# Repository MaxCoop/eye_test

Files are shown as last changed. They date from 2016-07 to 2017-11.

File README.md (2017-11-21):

# Pupil measurement device 
## System overview 
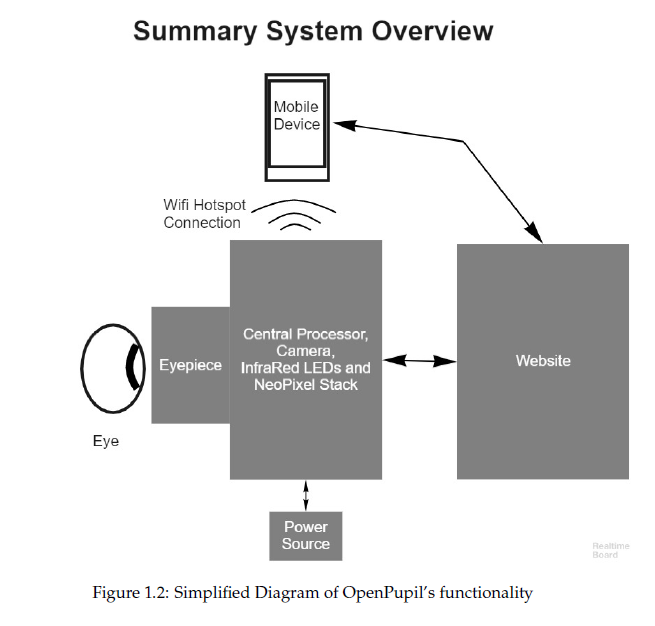
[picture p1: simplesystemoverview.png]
System

Format: 

# System description

Our system uses a RPi 2 B+ as a base along with a NoIR camera to recieve images of the pupil illuminated under IR light. RPi setup instuctions [here](https://github.com/kaiwhata/eye_test/blob/master/RPi_setup.md). Our continous integration and testing pipline is detailed [here](https://github.com/kaiwhata/eye_test/blob/master/testing.md). We use neopixel rings to illuminate the eye with visible light and them image process the camera frame stream to measure the pupil size based of several different algorithms (listed below). The Rpi acts as its own wifi hotspot for the 'Openpupil' network. Once connected to the network, the device is controlled by a python flask webapp acessible through a browser at the ip address `192.168.42.1:5000/`. The flask webapp code is contained within the `app.py` file, whereas site dynamics are controlled via javascript in the `index.html` and calls some additional javascript functions from the `extra.js` file. The webapp can be launched by running the command `sudo python app.py` from inside the webapp directory. We also use `supervisor-ctl` to run this app at boot by default.  

# Software process

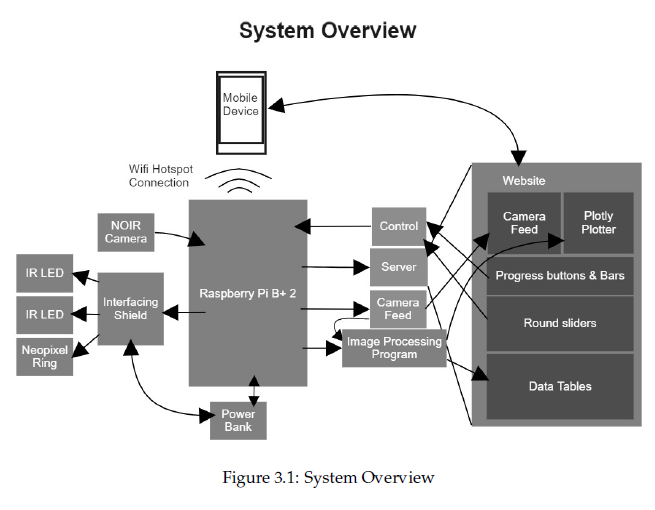
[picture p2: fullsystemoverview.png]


```
.
+-- _Webapp
|   +-- RunMe.sh
|   +-- App.py
|   +-- camera.py
|   +-- camera_pi.py
|   +-- _python
|   |   +-- NeopixelColorControl.py
|   |   +-- data_plotting.py
|   +-- _templates
|   |   +-- index.html
|   +-- _Data
|   |   +-- <date_named_data_folders>
|   +-- _static
|   |   +-- _js
|   |   |   +-- extra.js
|   |   |   +-- script.js
|   |   +-- _css
|   |   +-- _dist
|   |   +-- _images
|   |   +-- _scripts
|   |   +-- _src
+-- _Snapshot
```

## Supervisor
We use supervisor-ctl to launch the flask webserverapp at boot.
Scripts are called automatically from the `supervisord.conf` file and running the `supervisorctl status all` command will show what scripts/p[rograms are currently known by and teh status of them under supervior.

## Scripts
Main script is `RunMe.sh` which currently uses the `/CCodeVid5` command for ?? fps image capture and generates datafiles in teh data directory based on time and date. Illumintation is controlled by and calling the script `neopixel_elf.py` from the neopixel driver directory to perform the specific light sequences. 

## Video frame processing
Currently frames are parsed directly from the rpi camers by the CCodeVid5.cpp method  
The process sequence is performed using OpenCV methods:
  - extract red channel
  - binary thresholding - `threshold(50)` but dynamically calculated from the darkest 6000 pixels
  - count number of black pixels after thresholding (analog of pupil area)
  - estimate centre location of pupil and pupil width and height each frame based of x and y intensity histograms
  - in the past we have also attempted canny edge detction followed by hough circle fitting
  - ultimately we will also implements Kaps' spiral edge following code for higher resolution and faster measurement 

# Hardware System description
System designs and code for a cheap pupil measurement device that is capable of fabrication and use by non-technical people.
Current system design uses a 3D printed google (the OpenSCAD files), and a 16 neopixel ring for colour specific illumination, two wide angle IR LEDs controlled using a transistor and a 15 Ohm resistor.  IR LED is driven by GPIO pin 4, Neopixels are driven from GPIO 18. The google also contains the lens from a Google cardboard and photographic negative film to block visible light to the NoIR camera used for image capture.

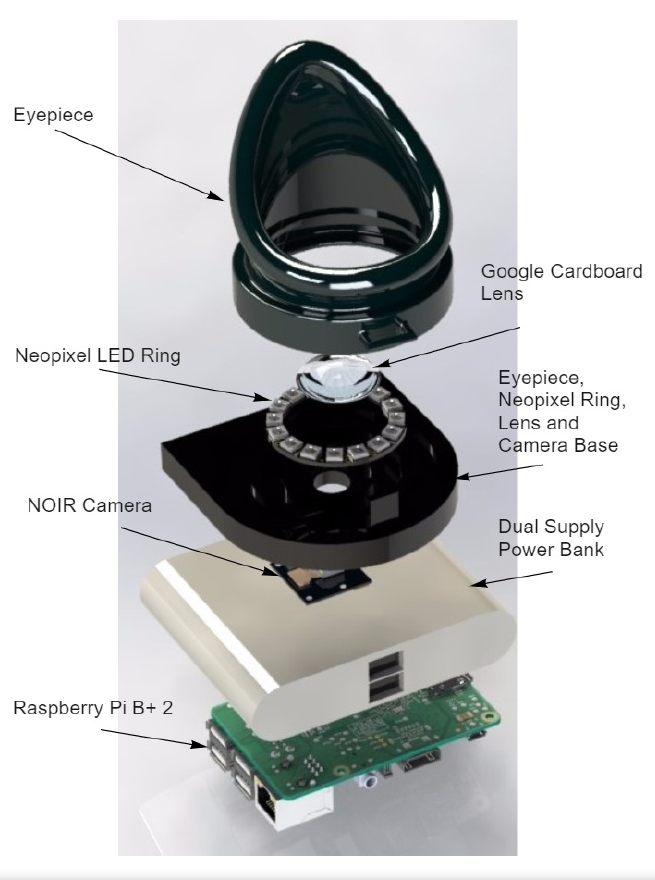
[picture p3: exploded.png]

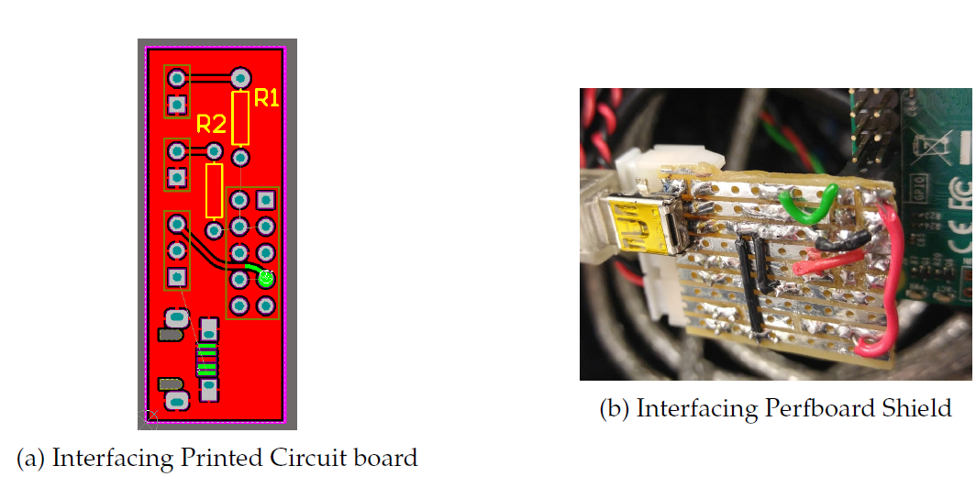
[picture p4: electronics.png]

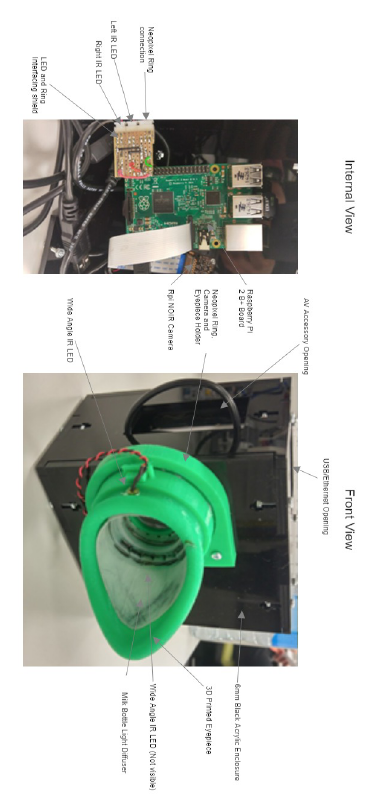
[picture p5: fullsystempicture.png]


Neopixels used in this project have the datasheet from here - https://cdn-shop.adafruit.com/datasheets/WS2812.pdf

Intensity measurement for blue light = 200-400 mCD (milliCandela) according to the Neopixel datasheet

3D Model for Neopixel used in this project can be found here: https://grabcad.com/library/neopixelring-16x-1/details?folder_id=1182174

3D Model for Eyepiece used in this project can be found here: https://grabcad.com/library/eyecup

3D Model for Raspberry Pi used in Assembly can be found here: https://grabcad.com/library/raspberry-pi-model-b-2

System uses Raspberry PI 2 B. Pinout used here -> http://pi4j.com/images/j8header-2b-large.png

### To Do
 - fix security an permissions (sudo) issues
 - improve javascript app load time by caching
 - upgrades to binocularity via multiplexer and multiple neopixel rings
 - implement spiral edge detection alcorithing for `CCodeVid6.cpp`
 - fix bug where preview button locks camera process
 - the 'measure' button needs 'close preview' functionality added to it so that it frees the camera for CCodeVid analysis
  
Credit to Dr. Jesse Gale for original concept and implementation idea. To Kapetini Polutea for the image processing code and algorithims. To Shaetrun Pathmanathan for the electronics and hardware redesign and for the web interface and javascript.

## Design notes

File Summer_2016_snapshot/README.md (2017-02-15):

# Pupil measurement device

#Dec 2016 update

#Software process

Experimentation has shown that for low resolution videos (480p, 720p, 1080p) the number of black pixels is a slow and innacurate method of pupil mesurement. Whilst improvments to the eyepiece (specifically the addition of another IR led) has improved thresholding it appears very noisy compared to full resolution data.

Current experiments have implemented the Hough circle dection algorithm 9using canny edge detection) to detect a single circle in our original image (code in `measure_pupil_hough.py`). We expect this to be unusably slow on the Rpi.

Kaps has implemented image capture and near real-time processing on 480p video `CCodeVid2.cpp`. OUr current pupil detection algotithim has an unacceptable signal to noise ratio in these low resolution videos. 

# Image processing
Currently images are parsed by the `measure_pupil_hough.py` script [`python measure_pupil_hough.py Handsomebroscaled.png`] 
The `Handsomebroscaled.png` file is an example input for processing
The process sequence is performed using OpenCV methods:
  - extract black pixels band using `cv2.inRange()`
  - [median blur appears unncesessary here median filter (5) - `medianBlur()` , gaussian blur gives worse results]
  - Hough circle matching with initial parameters [1.5, 1000, 30, 15, 5, 100]
  - this currently omits image normalisation equaliseHist() 

#Hough parameters
A `dp` of 1.5 or 1.9 appears optimimal for early testing. Higher and lower values (with the exception of 1.3) give reasonable resukts but a worse fit. The circle distance parameter has no clear effect (so 1000 is fine for the moment).                        param1=30,param2=15,minRadius=5,maxRadius=100.

## To Do
 - [ ] Test Hough algorthim speed on RPi and vary parameters for performance.
 - [ ] Test hough algorthim for noise in 480p videi on RPi
 - [ ] Gather reproducibility data using python video processing code
 - [ ] Multithreaded image processing and capture

--------

#Current Process
Capture on rpi with `flash.sh` using protocol defined in `neopixel.py` in the comms subdirectory to generate a .h264 type video file. Convert to .m4v type using VLC on OSX and then process using the `video_process.py` script with an estimated threshold of 50.

# System description
System designs and code for a cheap pupil measurement device that is capable of fabrication and use by non-technical people.
Current system design uses a 3D printed google (the OpenSCAD files), and two neopixels for colour specific illumination, an IR LED controlled using a transistor and a 15 Ohm resistor.  IR LED is driven by GPIO pin 4, Neopixels are driven from GPIO 18. The google also contains the lens from a Google cardboard and photographic negative film to block visible light to the NoIR camera used for image capture.

Neopixels used in this project have the datasheet from here - https://cdn-shop.adafruit.com/datasheets/WS2812.pdf

Intensity measurement for blue light = 200-400 mCD (milliCandela) according to the Neopixel datasheet

3D Model for Neopixel used in this project can be found here: https://grabcad.com/library/neopixelring-16x-1/details?folder_id=1182174

3D Model for Eyepiece used in this project can be found here: https://grabcad.com/library/eyecup

3D Model for Raspberry Pi used in Assembly can be found here: https://grabcad.com/library/raspberry-pi-model-b-2

System uses Raspberry PI 2 B. Pinout used here -> http://pi4j.com/images/j8header-2b-large.png

# Scripts
Main script is `flash.sh` which currently uses the `raspivid` command for 24 fps image capture to `outvid.h264` and calls the script `neopixel.py` from the `` directory to perform the specific light sequences. 

# Image processing
Currently images are parsed by the `measure_pupil.py` script [`python measure_pupil.py elf.jpg`] 
The `elf.jpg` file is an example input for processing
The process sequence is performed using OpenCV methods:
  - extract red channel
  - histogram normalisation - `equalizeHist()`
  - median filter (5) - `medianBlur()`
  - binary thresholding - `threshold(50)`
  - discarding the left half of the image (this should be done earlier)

Then black pixels from individual images are counted using `calcHist()`. This script also tries to identify the location of the pupil by returning the indexes of the maximum black pixel for image rows and columns and then plotting an area equivalent circle at that location. This will systematically overestimate the pupil measurement due to black pixel noise.

# Video processing
Videos are processed using the same process, but via the `video_process.py` script [`python video_process.py inputvid.hm4v thresholdvalue`]. This script also writes the processed frames to an m4v file for later inspection and produces a plot of the number of frames vs the number of black pixels in each.

# Mobile device testing
We also examine the potential of using a mobile camera without the IR filter removed. 
Following standard methods for nightvision (RBG averages, min/max colour values) we may be able to replicate the NoIR camera results using a cheaper setup. This is currently accessed via the:
`python iphone_image_process.py image.jpg`

Credit to Dr. Jesse Gale for original concept and implementation idea.

#Other file notes
eye_image_process.py - an early test script attempting to normalise the image as one would for an infragram

python_image_grabber.py - a script for rapidly capturing video from the Rpi camera. This can be used in conjunction with the `flash.sh` script in place of the raspivid command however it currently does not yeild results comparable to that of the existing setup. It should provide higher framerates and closer to real-time resolution however.

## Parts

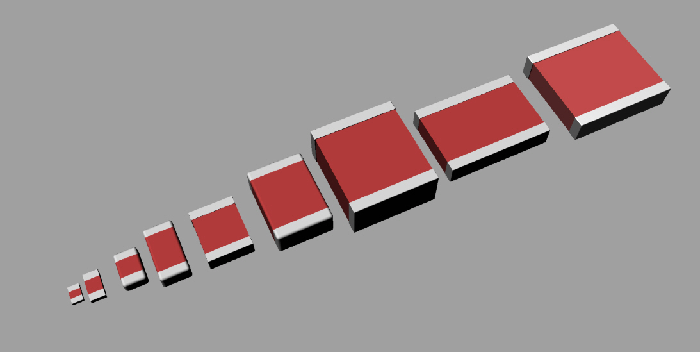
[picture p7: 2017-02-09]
Summer_2016_snapshot/3D Modelling Material/Neopixel Things/neopixelring-16x-1.snapshot.1/Neopixelring16x/Download/SMD_Capacitor/Capacitors SMD.jpg

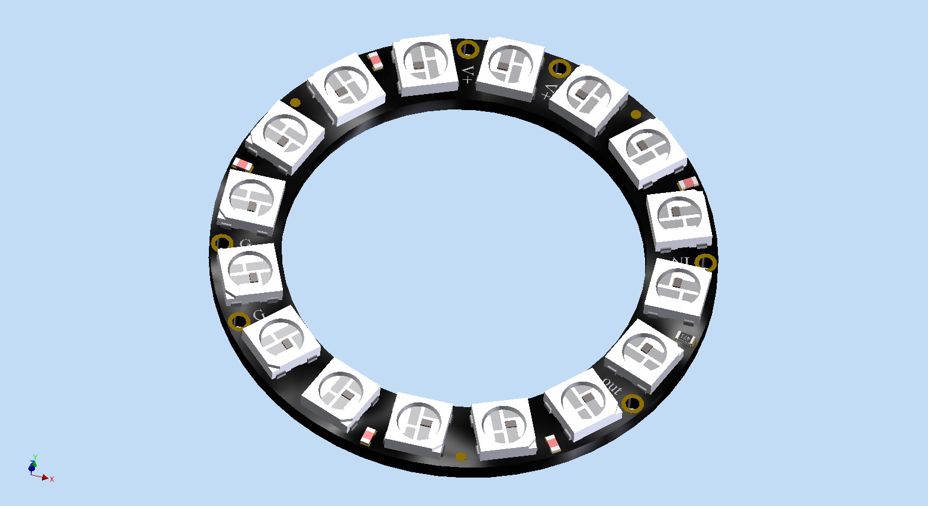
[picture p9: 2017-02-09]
Summer_2016_snapshot/3D Modelling Material/Neopixel Things/neopixelring-16x-1.snapshot.1/Neopixelring16x/Dokumentation/NeoPixel16x_front.bmp

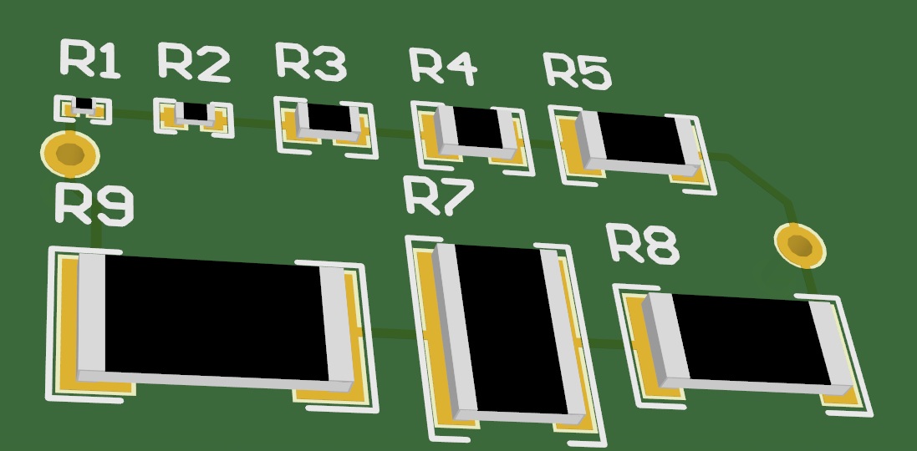
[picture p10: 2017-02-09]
Summer_2016_snapshot/3D Modelling Material/Neopixel Things/neopixelring-16x-1.snapshot.1/Neopixelring16x/Download/SMD_Resistor/resistors SMD2.jpg

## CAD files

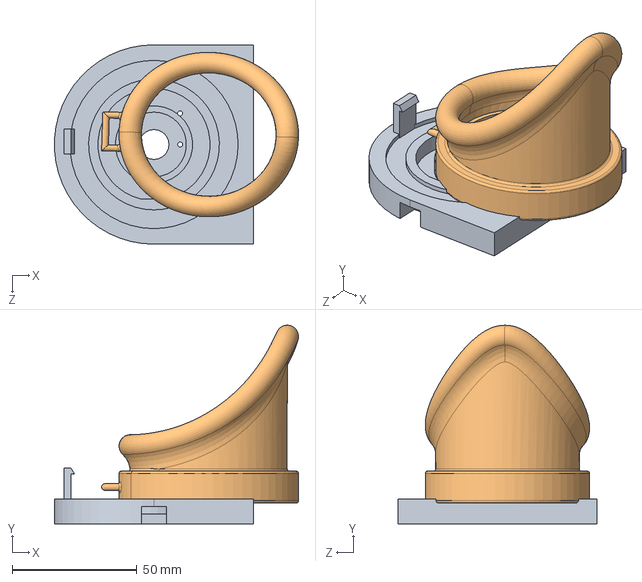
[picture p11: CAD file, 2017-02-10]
Summer_2016_snapshot/3D Modelling Material/Eyepiece and Holder Revisions/Eyepiece and Ringholder v1.1.SLDASM
97.9 x 79.7 x 80.0 mm
LED-16Ring-Cam Holder V1.1
Eyepiece V1.4

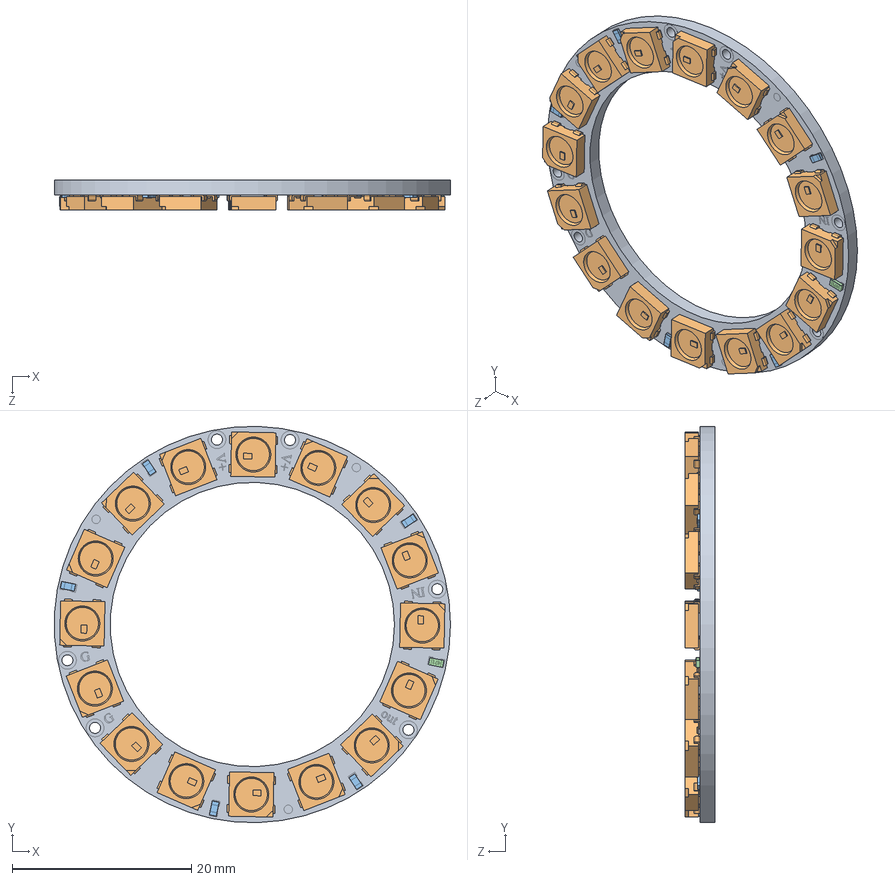
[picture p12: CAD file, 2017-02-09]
Summer_2016_snapshot/3D Modelling Material/Neopixel Things/NeoPixel16x.SLDASM
44.2 x 44.2 x 3.36 mm
LED-Halter_Ring
WS2812_RGB_LED x 16
CAP0603 x 5
RES0603_471

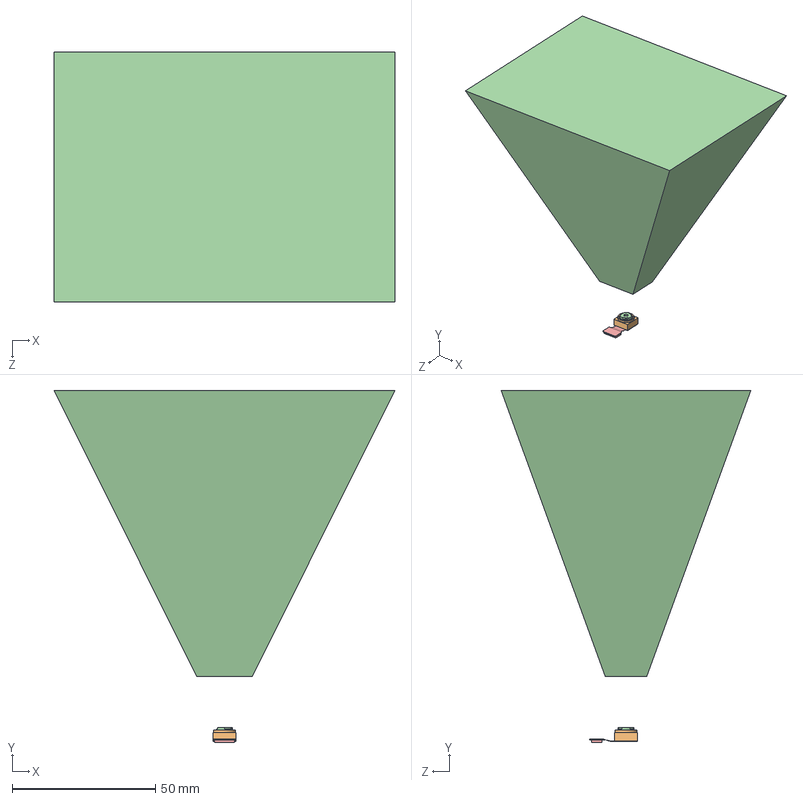
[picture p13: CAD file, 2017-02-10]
Summer_2016_snapshot/3D Modelling Material/raspberry-pi-camera-1.snapshot.15/OVA5647.SLDASM
119.2 x 123.2 x 87.4 mm
OVA5647
OVA5647_Housing
OVA5647_IR-Glas
OVA5647_Lens
OVA5647_Pigtail

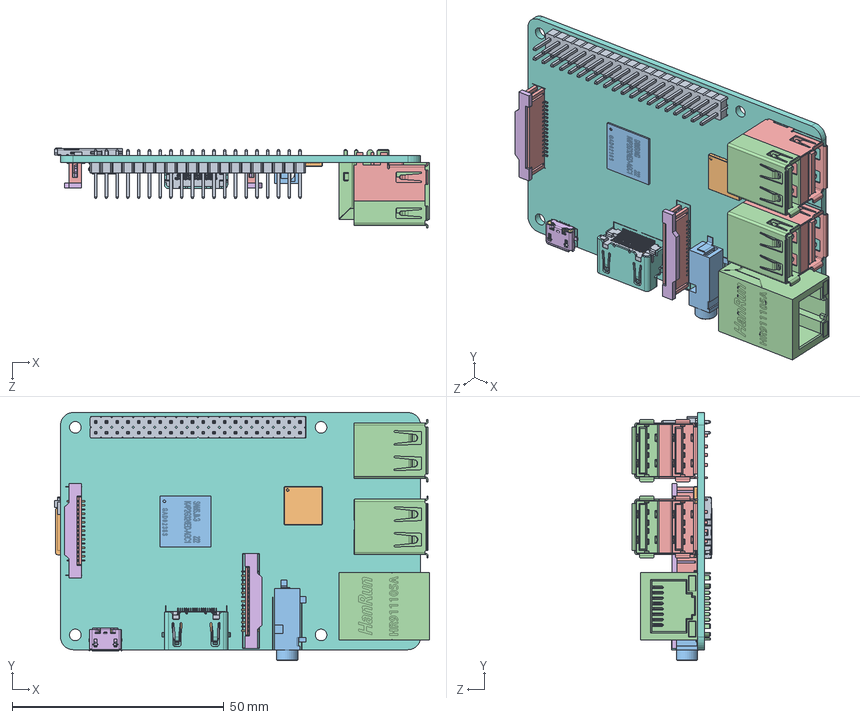
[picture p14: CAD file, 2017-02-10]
Summer_2016_snapshot/3D Modelling Material/raspberry-pi-model-b-2.snapshot.16/raspberrypi_b_+_(assembly).SLDASM
88.5 x 58.5 x 18.9 mm
raspberry_pi_B+_(bar_180_2x20)
raspberry_pi_B+_(QFN64)
raspberry_pi_B+_(168_FBGA_12x12)
raspberry_pi_B+_(USB_x2_part1) x 2
raspberry_pi_B+_(USB_x2_part2) x 2
raspberry_pi_B+_(micro_USB_cover)
raspberry_pi_B+_(micro_USB_contacts)
raspberry_pi__HDMI_socket_cover
raspberry_pi__HDMI_socket_inside
raspberry_pi__HDMI_socket_large_pin x 10
raspberry_pi__HDMI_socket_small_pin x 9
raspberry_pi_B+_(RJ45)
raspberry_pi__15_pin_FFC_Connector_body x 2
raspberry_pi__15_pin_FFC_Connector_locker x 2
raspberry_pi__15_pin_FFC_Connector_pins x 30
raspberry_pi_B+_(CI_Board)
raspberry_pi_B+_(microsd_slot2)
raspberry_pi_B+_(microsd2)
raspberry_pi_B+_(audio_video2)

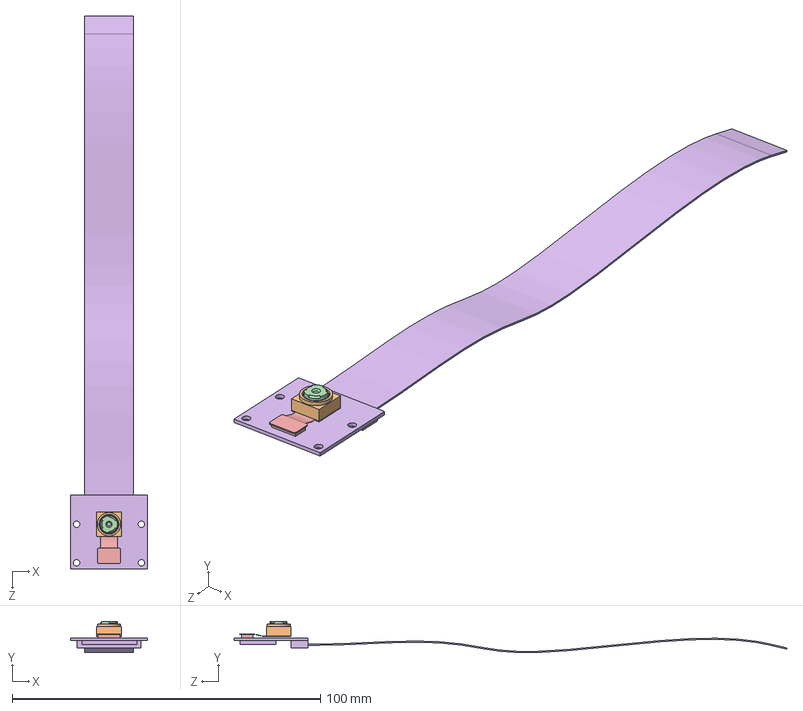
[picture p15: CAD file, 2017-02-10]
Summer_2016_snapshot/3D Modelling Material/Enclosure packaging/RasPi_Camera.SLDASM
25.0 x 10.1 x 179.3 mm
OVA5647
OVA5647_Housing
OVA5647_IR-Glas
OVA5647_Lens
OVA5647_Pigtail
RasPi_Camera_Board

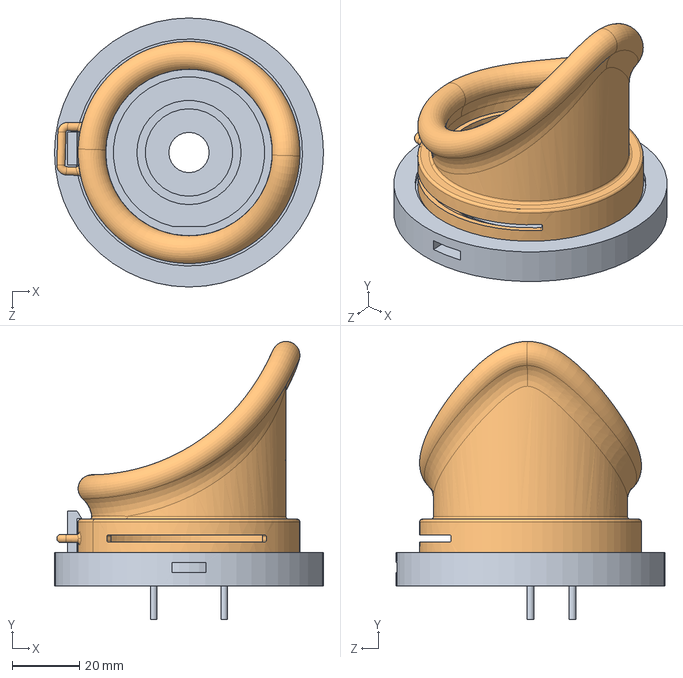
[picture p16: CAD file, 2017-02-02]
Summer_2016_snapshot/3D Modelling Material/Eyepiece and Holder Revisions/Eyepiece and Neoholder.SLDASM
80.0 x 82.7 x 80.0 mm
LED-16Ring-Cam Holder V1.0
Eyepiece V1.1

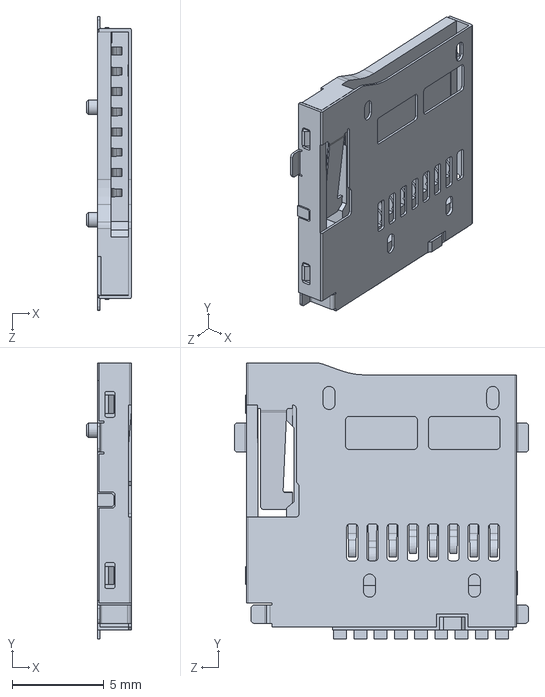
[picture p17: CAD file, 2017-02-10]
Summer_2016_snapshot/3D Modelling Material/raspberry-pi-model-b-2.snapshot.16/raspberry_pi_B+_(slot).SLDASM
2.44 x 15.0 x 16.0 mm

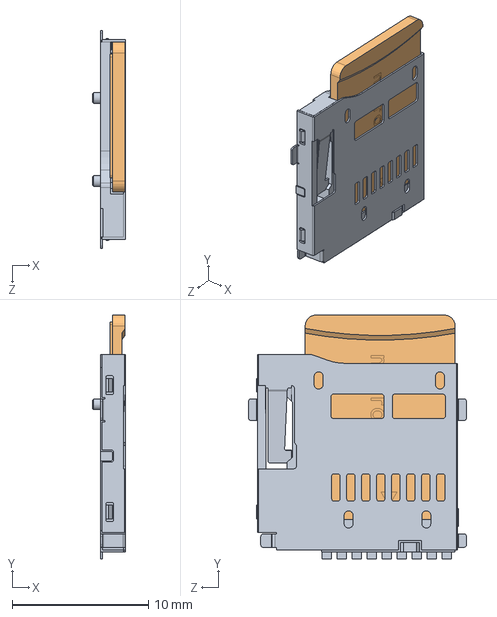
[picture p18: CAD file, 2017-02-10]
Summer_2016_snapshot/3D Modelling Material/raspberry-pi-model-b-2.snapshot.16/raspberry_pi_B+_(microsd_slot).SLDASM
2.44 x 17.9 x 16.0 mm
raspberry_pi_B+_(slot)
raspberry_pi_B+_(microsd)

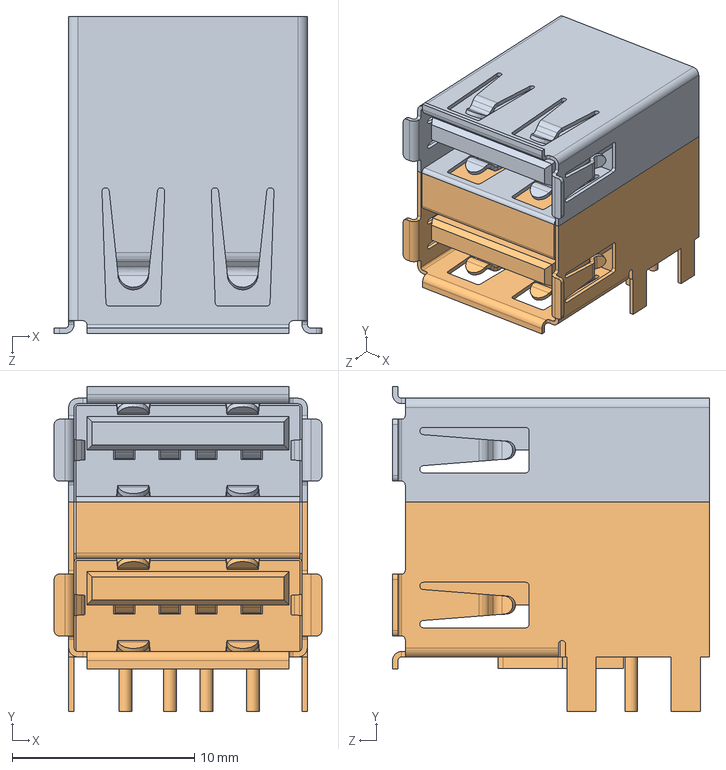
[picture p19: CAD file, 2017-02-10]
Summer_2016_snapshot/3D Modelling Material/raspberry-pi-model-b-2.snapshot.16/raspberry_pi_B+_(USB_x2).SLDASM
14.7 x 17.9 x 17.4 mm
raspberry_pi_B+_(USB_x2_part1)
raspberry_pi_B+_(USB_x2_part2)

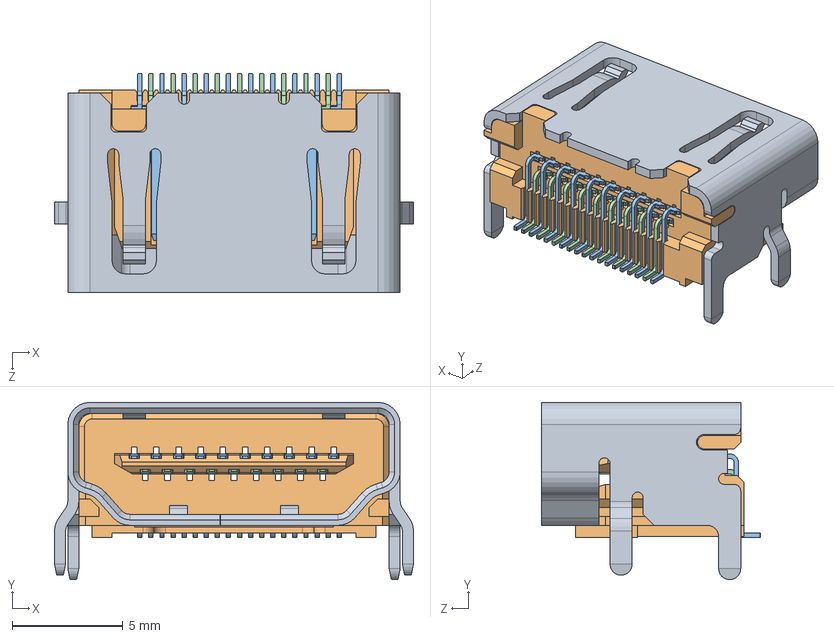
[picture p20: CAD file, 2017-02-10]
Summer_2016_snapshot/3D Modelling Material/raspberry-pi-model-b-2.snapshot.16/raspberry_pi_B+_(HDMI_socket).SLDASM
16.2 x 8.00 x 9.90 mm
raspberry_pi__HDMI_socket_cover
raspberry_pi__HDMI_socket_inside
raspberry_pi__HDMI_socket_large_pin x 10
raspberry_pi__HDMI_socket_small_pin x 9

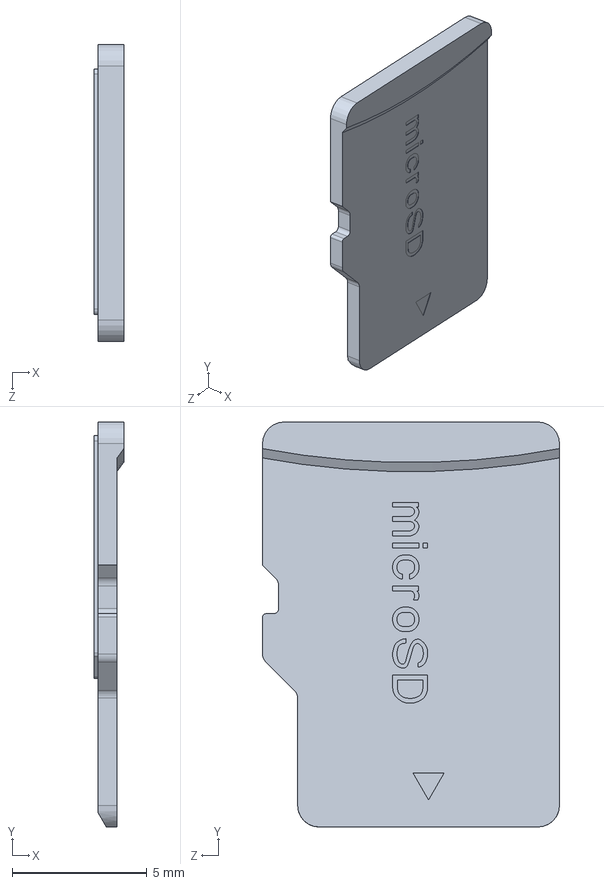
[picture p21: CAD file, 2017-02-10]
Summer_2016_snapshot/3D Modelling Material/raspberry-pi-model-b-2.snapshot.16/raspberry_pi_B+_(microsd).SLDASM
1.10 x 15.0 x 11.0 mm

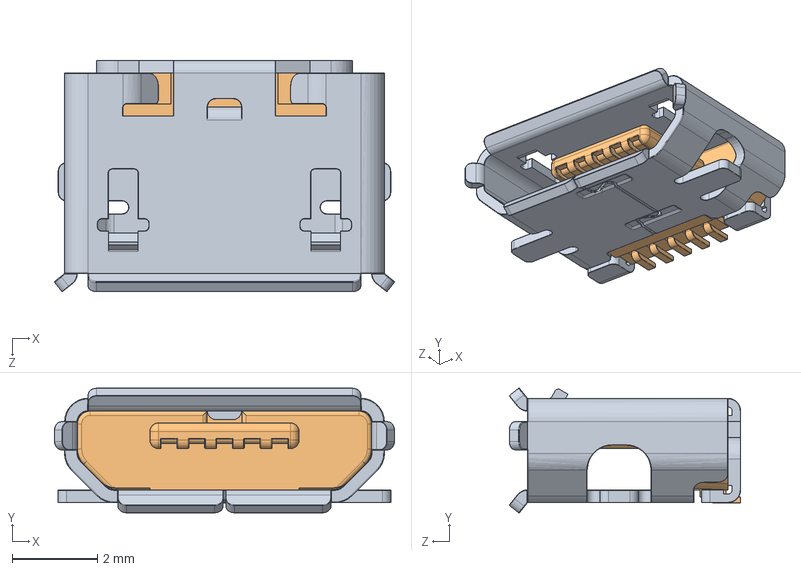
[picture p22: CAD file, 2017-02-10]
Summer_2016_snapshot/3D Modelling Material/raspberry-pi-model-b-2.snapshot.16/raspberry_pi_B+_(micro_USB).SLDASM
7.97 x 2.92 x 5.43 mm
raspberry_pi_B+_(micro_USB_cover)
raspberry_pi_B+_(micro_USB_contacts)

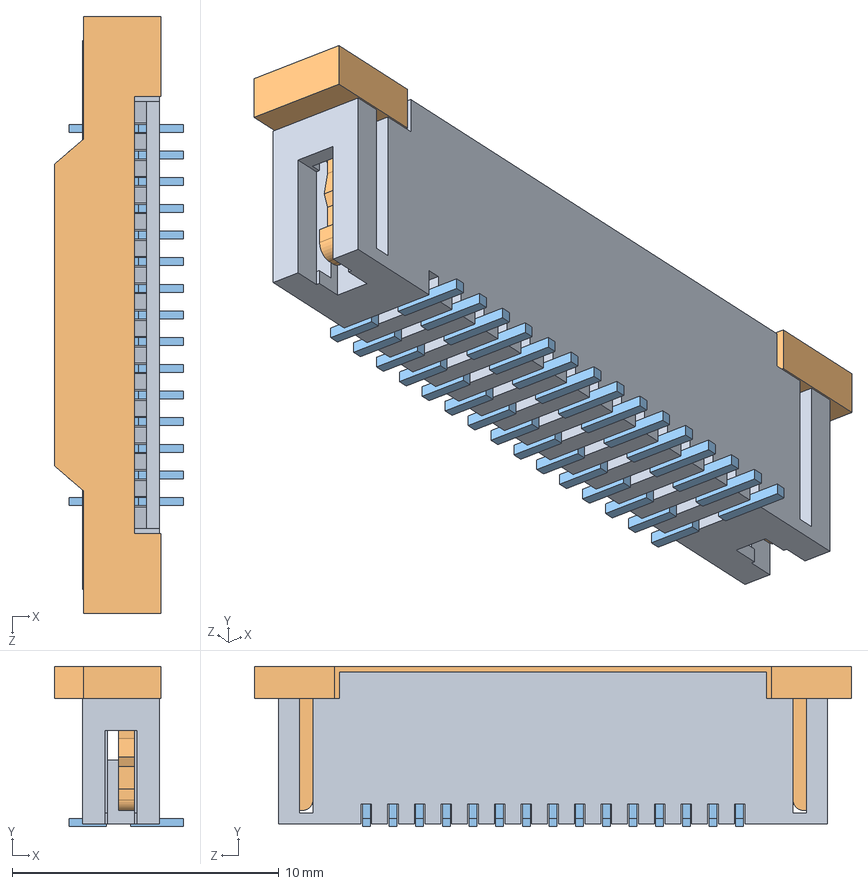
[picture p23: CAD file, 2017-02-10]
Summer_2016_snapshot/3D Modelling Material/raspberry-pi-model-b-2.snapshot.16/raspberry_pi_B+_(15_pin_FFC_Connector).SLDASM
4.85 x 6.00 x 22.4 mm
raspberry_pi__15_pin_FFC_Connector_body
raspberry_pi__15_pin_FFC_Connector_locker
raspberry_pi__15_pin_FFC_Connector_pins x 15

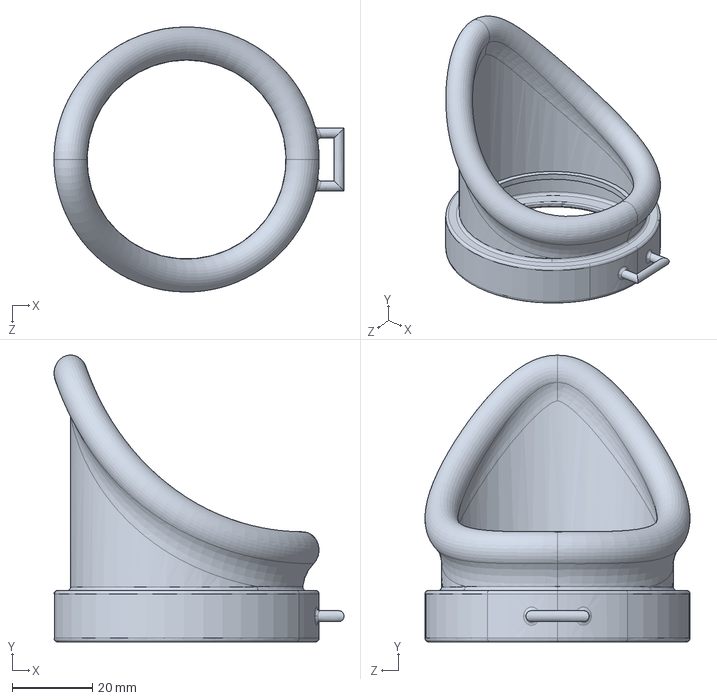
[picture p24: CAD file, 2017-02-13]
Summer_2016_snapshot/3D Modelling Material/Enclosure packaging/Eyepiece V1.3.SLDPRT
72.2 x 71.4 x 66.0 mm

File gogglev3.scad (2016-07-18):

//goggles
//union(){}
//intersection(){

//cylinder(height, r1, r2, center=true/false)


union(){

union(){
translate([8,0,0]) rotate([90,90,90]) cylinder(1,12,12);
difference(){
translate([0,0,0]) rotate([90,90,90]) cylinder(8,16,12);
translate([0,0,0]) rotate([90,90,90]) cylinder(8,14,10);
}
}

//translate([-16,0,0])
difference(){
difference(){
translate([-12,0,0]) rotate([90,90,90]) cylinder(12,20,16);
translate([-12,0,0]) rotate([90,90,90]) cylinder(12,18,14);
}


translate([-20,2,0]) rotate([97,90,90]) cylinder(20,28,14);
}

}

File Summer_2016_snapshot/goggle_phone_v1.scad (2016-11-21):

//goggles
//union(){}
//intersection(){
//cylinder(height, r1, r2, center=true/false)
//cube([,,])

//focal cone
tip_radius = 20;
tip_thickness = 4;
centre_radius = 32;
wall_thickness = 4;
tip_length = 0; //akin to distance between eye and mounted lens

//lens
seating_depth = 5;
lens_radius = 13;

//camera aperture
aperture_radius = 8;

//mount details
phone_mount_location = 15;
mount_width = 7;
mount_depth =5;

//phone details
phone_depth = 12;
mount_height = phone_depth;
claw_length = 10;
claw_depth = mount_depth;
base_depth = tip_radius - lens_radius;

union(){

difference(){

//end disk
translate([tip_length,0,0]) rotate([90,90,90]) cylinder(tip_thickness,tip_radius,tip_radius);

//lens inset
translate([tip_length-tip_thickness/2,0,0]) rotate([90,90,90]) cylinder(seating_depth,lens_radius,lens_radius);

//camera aperture
translate([tip_length-tip_thickness/2,0,0]) rotate([90,90,90]) cylinder(10,aperture_radius,aperture_radius);

}//closes difference for lens mount

translate([tip_length-mount_height,phone_mount_location-mount_width/2,mount_depth/2]) rotate([90,90,90]) cube([mount_width, mount_depth,mount_height]);
translate([tip_length-mount_height-claw_depth,phone_mount_location-mount_width/2-claw_length/2,mount_depth/2]) rotate([90,90,90]) cube([mount_width, claw_length,claw_depth]);
translate([tip_length-mount_depth,phone_mount_location-base_depth/2,mount_depth/2]) rotate([90,90,90]) cube([mount_width, base_depth,claw_depth]);


translate([tip_length-mount_height,-mount_width/2,phone_mount_location+mount_depth/2]) rotate([90,90,90]) cube([mount_depth, mount_width,mount_height]);
translate([tip_length-mount_height-claw_depth,-mount_width/2,phone_mount_location+mount_depth/2]) rotate([90,90,90]) cube([ claw_length,mount_width, claw_depth]);
translate([tip_length-mount_depth,-mount_width/2,phone_mount_location+0.75*base_depth]) rotate([90,90,90]) cube([mount_width, base_depth,claw_depth]);

}//closes union with phone holder

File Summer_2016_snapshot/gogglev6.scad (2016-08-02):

//goggles
//union(){}
//intersection(){
//cylinder(height, r1, r2, center=true/false)
//cube()

//focal cone
tip_radius = 28;
tip_thickness = 4;
centre_radius = 32;
wall_thickness = 4;
tip_length = 30; //akin to distance between eye and mounted lens

//eyepiece size
eyepiece_length = 24;
eyepiece_end_radius = 40;

//eyepiece shape
cut_cylinder_radius = 40;
cut_offset = 12;

//lens
seating_depth = 5;
lens_radius = 13;

//led size
led_radius = 4;
led_inset = 3;
pin_width = 1;

//neopixel size
neopixel_radius = 7;
neopixel_inset = 4;
neopixel_location = 13;

//camera aperture
aperture_radius = 5;

//rpi camera mount
cube_size = 27;
mount_height = 10;
mount_wall_thickness = 1;

//LED diffuser - removed - doesn't work
//diffuser_height = 15;
//diffuser_radius = 12;

//upper_diameter = 0.13*(diffuser_height+tip_thickness+1)+tip_radius-1;
//lower_diameter = 0.13*diffuser_height+tip_radius-1;

difference(){
union(){ //adds pegs for rpi camera mount

union(){

difference(){

union(){
//end disk
translate([tip_length,0,0]) rotate([90,90,90]) cylinder(tip_thickness,tip_radius,tip_radius);

//focal tip
difference(){
//subtract one cone from another for hollow cylinder
translate([0,0,0]) rotate([90,90,90]) cylinder(tip_length,centre_radius,tip_radius);
translate([0,0,0]) rotate([90,90,90]) cylinder(tip_length,centre_radius-wall_thickness,tip_radius-wall_thickness);
}
}

//LED  inset
translate([tip_length-tip_thickness/2,tip_radius-1.5*wall_thickness-led_radius,0]) rotate([90,90,90]) cylinder(led_inset,led_radius,led_radius,$fn = 12);

//neopixel insets
translate([tip_length-tip_thickness/2,-neopixel_location,neopixel_location]) rotate([90,90,90]) cylinder(neopixel_inset,neopixel_radius,neopixel_radius,$fn = 12);
translate([tip_length-tip_thickness/2,-neopixel_location,-neopixel_location]) rotate([90,90,90]) cylinder(neopixel_inset,neopixel_radius,neopixel_radius,$fn = 12);

//lens inset
translate([tip_length-tip_thickness/2,0,0]) rotate([90,90,90]) cylinder(seating_depth,lens_radius,lens_radius);
}


//eyepiece
difference(){
//makes hollow cone cylinder as base eyepiece
difference(){
translate([-eyepiece_length,0,0]) rotate([90,90,90]) cylinder(eyepiece_length,eyepiece_end_radius,centre_radius);
translate([-eyepiece_length,0,0]) rotate([90,90,90]) cylinder(eyepiece_length,eyepiece_end_radius-wall_thickness,centre_radius-wall_thickness);
}
//controls shape of eyepiece
//vertical cylinder cut
translate([-cut_cylinder_radius,cut_offset,-cut_cylinder_radius]) rotate([0,0,90]) cylinder(80,cut_cylinder_radius,cut_cylinder_radius);
//sphere cut
//translate([-20,2,0]) sphere(22);
//cylinder cut
//translate([-20,2,0]) rotate([97,90,90]) cylinder(20,28,14);
}

}//closes eyepiece tip base union

//rpi camera mount
translate([tip_length+mount_height-tip_thickness/2+1,-2,2]) rotate([90,45,90]) cube(size = [cube_size, cube_size+1, mount_height], center = true);

//LED diffuser
/*
difference(){
translate([tip_length-diffuser_height,tip_radius-wall_thickness,0]) rotate([90,90,90]) cylinder(tip_thickness,diffuser_radius,diffuser_radius);
//subtraction ring
difference(){
translate([tip_length-diffuser_height-1,0,0]) rotate([90,90,90]) cylinder(tip_thickness+2,2*centre_radius,2*centre_radius);
translate([tip_length-diffuser_height-1,0,0]) rotate([90,90,90]) cylinder(tip_thickness+2,upper_diameter,lower_diameter);
}
}
*/

}//closes goggle mount union

//Rpi mounting bracket
//subtracts centre of mounting block
translate([tip_length+mount_height+1-tip_thickness/2+1,0,0]) rotate([90,45,90]) cube(size = [cube_size+3, cube_size-1, 1.2*mount_height], center = true);
//removes secondary block for neopixel pins
translate([tip_length+mount_height+1-tip_thickness/2+1,0,0]) rotate([90,45,90]) cube(size = [50, 10, 1.2*mount_height], center = true);


//LED pin holes
translate([tip_length-tip_thickness/2,tip_radius-1.5*wall_thickness-led_radius*0.5,0]) rotate([90,90,90]) cylinder(10,pin_width,pin_width);
translate([tip_length-tip_thickness/2,tip_radius-1.5*wall_thickness-led_radius*1.5,0]) rotate([90,90,90]) cylinder(10,pin_width,pin_width);

//neopixel pin holes
//Top
translate([tip_length-tip_thickness/2,-neopixel_location,neopixel_location+0.75*neopixel_radius]) rotate([90,90,90]) cylinder(20,pin_width,pin_width);
//Bottom
translate([tip_length-tip_thickness/2,-neopixel_location,neopixel_location-0.75*neopixel_radius]) rotate([90,90,90]) cylinder(20,pin_width,pin_width);
//Left
translate([tip_length-tip_thickness/2,-neopixel_location-0.75*neopixel_radius,neopixel_location]) rotate([90,90,90]) cylinder(20,pin_width,pin_width);
//Right
translate([tip_length-tip_thickness/2,-neopixel_location+0.75*neopixel_radius,neopixel_location]) rotate([90,90,90]) cylinder(20,pin_width,pin_width);


//Top
translate([tip_length-tip_thickness/2,-neopixel_location,-neopixel_location+0.75*neopixel_radius]) rotate([90,90,90]) cylinder(20,pin_width,pin_width);
//Bottom
translate([tip_length-tip_thickness/2,-neopixel_location,-neopixel_location-0.75*neopixel_radius]) rotate([90,90,90]) cylinder(20,pin_width,pin_width);
//Left
translate([tip_length-tip_thickness/2,-neopixel_location-0.75*neopixel_radius,-neopixel_location]) rotate([90,90,90]) cylinder(20,pin_width,pin_width);
//Right
translate([tip_length-tip_thickness/2,-neopixel_location+0.75*neopixel_radius,-neopixel_location]) rotate([90,90,90]) cylinder(20,pin_width,pin_width);

//camera aperture
translate([tip_length-tip_thickness/2,0,0]) rotate([90,90,90]) cylinder(10,aperture_radius,aperture_radius);

}

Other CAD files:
Summer_2016_snapshot/3D Modelling Material/raspberry-pi-model-b-2.snapshot.16/raspberry_pi_B+_(P1).SLDASM
Summer_2016_snapshot/3D Modelling Material/Neopixel Things/neopixelring-16x-1.snapshot.1/Neopixelring16x/Dokumentation/NeoPixel16x.stp
Summer_2016_snapshot/3D Modelling Material/Eyepiece and Holder Revisions/goggle.scad
Summer_2016_snapshot/3D Modelling Material/Enclosure packaging/Baseplate Frame.SLDPRT
Summer_2016_snapshot/3D Modelling Material/Enclosure packaging/Enclosure Base.SLDPRT
Summer_2016_snapshot/3D Modelling Material/Enclosure packaging/Enclosure Eastplate.SLDPRT
Summer_2016_snapshot/3D Modelling Material/Enclosure packaging/Enclosure Screenplate.SLDPRT
Summer_2016_snapshot/3D Modelling Material/Enclosure packaging/Enclosure Westplate.SLDPRT
Summer_2016_snapshot/3D Modelling Material/Enclosure packaging/Eyepiece V1.4.SLDPRT
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

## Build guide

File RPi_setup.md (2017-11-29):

# Instructions for setting up the background RPi

* Start with fresh raspian install (we're using 2015-09-24-raspian-jessie.img for the RPi 2B+)
* Start with fresh raspian install (we're using 2017-09-07-raspian-jessie.img for the RPi 3)

* `sudo raspi-config` + resize SD card partition and enable camera and ssh 
* `sudo apt-get update`
* `sudo apt-get upgrade`
* `sudo apt-get install git-core git`
* `sudo apt-get install libopencv-dev cmake`
* if using the multiplexer run  `sudo apt-get install i2c-tools python-smbus`
* if not using the multiplexer run `sudo apt-get install python-picamera`

## For the cpp code to work
* download the raspicam library [here](https://sourceforge.net/projects/raspicam/files/?)
* then run the following commands:
  * `tar xvzf raspicam-0.1.6.zip`
  * `cd raspicam-0.1.6.zip`
  * `mkdir build`
  * `cd build`
  * `cmake ..`
  * `make`
  * `sudo make install`
  * `sudo ldconfig`

### Then install supervisor
 * `pip install supervisor`
 * Then create `/etc/supervisord.conf` and populate appropriately

### Then install flask
 * `pip install flask`

### To set the pi up as its own wifi hotspot
 * `sudo apt-get install hostapd isc-dhcp-server`

## Then clone code from repo
* `git clone https://github.com/kaiwhata/eye_test`
* `git status`

You will also need to get the neopixel control library downloaded and working by following instructions here:
* https://learn.adafruit.com/neopixels-on-raspberry-pi/overview
* and make sure to install the python wrappers so that the example neopixel.py command works

To add code to the repo:
* `git push` then enter username and password

To pull new code from the repo:
* `git pull`

To use the camera from C programs the `camera.h` file must be in the same directory as the script runs from.
* `#include "camera.h"` this is the camera import line.

Once you're ready to have the pi as it's own wifi hotspot follow the setup instructions here.
 * https://learn.adafruit.com/setting-up-a-raspberry-pi-as-a-wifi-access-point/overview
 * ONLY DO THIS ONCE YOU ALREADY HAVE EVERYTHING YOU NEED FROM THE INTERNET IF YOU ARE NOT USING AN ETHERNET CONNECTION
 (not that it's hard to undo - it's just a pain to constantly reconfigure your `/etc/network/interfaces` files
 
## Additional Python Libraries (optional for development)
* `sudo apt-get install python-opencv python-scipy python-numpy ipython python-setuptools python-matplotlib python-picamera`

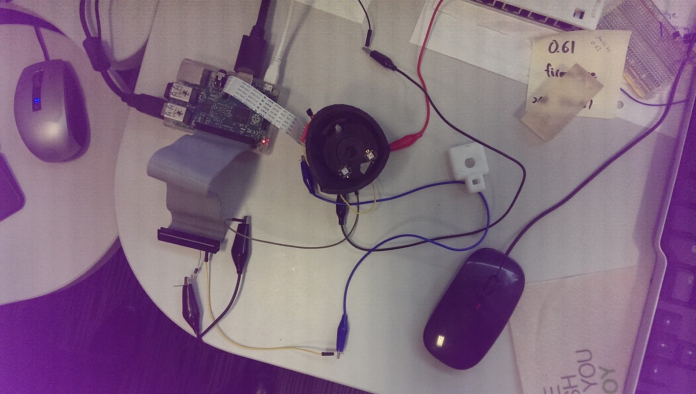
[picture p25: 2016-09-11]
Summer_2016_snapshot/setup.jpg

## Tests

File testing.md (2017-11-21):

# Continuous Integration Pipeline

In order to make our software pipeline and code more robust we use the following tests and tools.

## Python

All our python code is validated using `Pylint` prior to being committed to the repo.
Once a commit is made we use Travis CI to automatically run all unit tests against our new release.
For website tests we use `Selenium`, and `Doctest`

## C++ - none of the following has been done yet

We check all our C++ code with either `cpplint` [Google style guide] or `cppcheck` [`sudo apt get install cppcheck`]
Once a commit is made we use Travis CI to automatically run all unit tests against our new release.

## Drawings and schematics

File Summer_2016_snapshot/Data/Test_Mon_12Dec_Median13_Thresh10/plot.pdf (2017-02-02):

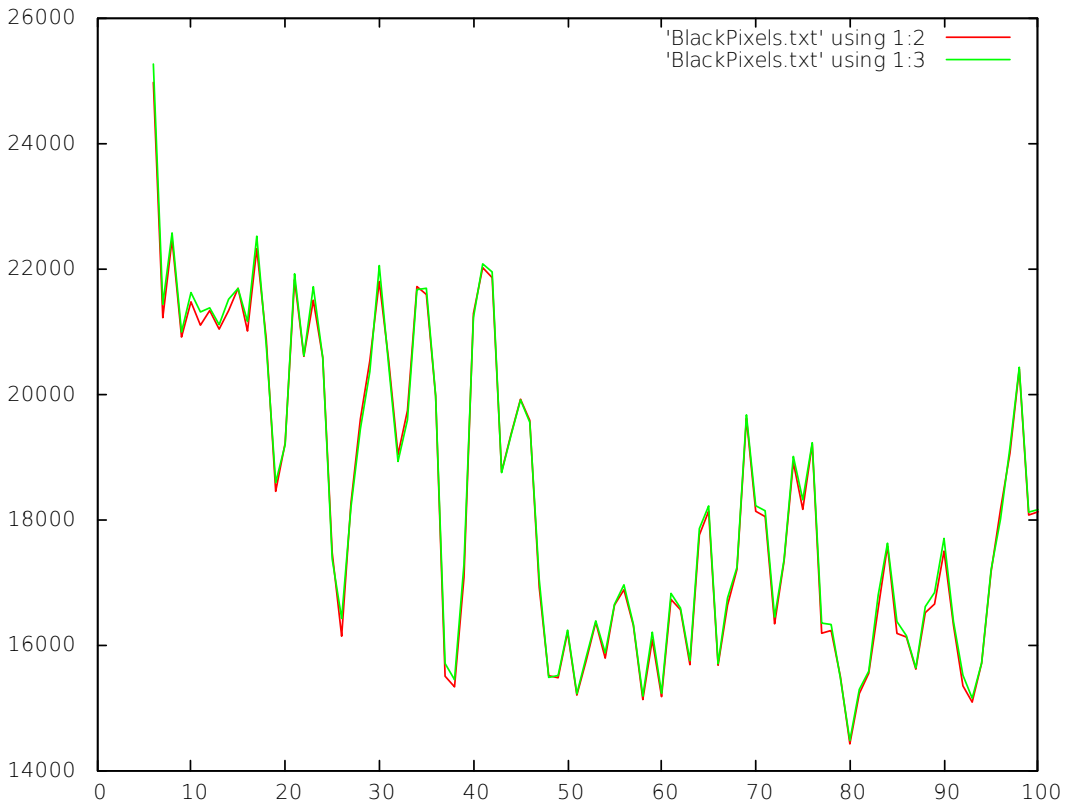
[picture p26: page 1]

'BlackPixels.txt' using 1:2
'BlackPixels.txt' using 1:3

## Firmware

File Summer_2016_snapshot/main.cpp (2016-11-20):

// Library for ENGR101 robot challenge using Raspberry PI
// Author: A.Roberts, arthur.roberts@ecs.vuw.ac.nz

#include <stdio.h>
#include <unistd.h>
#include <pigpio.h>
#include "camera.h"
#include <fcntl.h>
#include <linux/fb.h>
#include <sys/ioctl.h>
#include <sys/mman.h>
#include <sys/socket.h>
#include <arpa/inet.h>
#include <errno.h>


#define CAMERA_WIDTH 320 //Control Resolution from Camera
#define CAMERA_HEIGHT 240 //Control Resolution from Camera

// camera stuff
CCamera *cam;  // camera instance
int  Y_row[CAMERA_WIDTH];
char pixels_buf[CAMERA_WIDTH*CAMERA_HEIGHT*4];

// camera image converted to fit display depth - somewhat big for 1960x1050 screen
char cam_disp[3528000];
// original image on the screen
char original[3528000];
int fbfd = 0;
struct fb_var_screeninfo orig_vinfo;
char *fbp = 0;
struct fb_var_screeninfo vinfo;
struct fb_fix_screeninfo finfo;
long int screensize;
int res;

// hardware
int spi_h; // handle of SPI

int sock;  // socket handle

// how much diagnostic to display
int disp_level;

extern "C"
{

int init_hardware()
{

    if (gpioInitialise() < 0)
    {
      printf("GPIO initialization failed \n");
      return -1;
    }
    //gpioSetMode(24,PI_OUTPUT);

    // set motor pins
    gpioSetMode(12,PI_OUTPUT);
    gpioSetMode(16,PI_OUTPUT);
    gpioSetMode(20,PI_OUTPUT);
    gpioSetMode(21,PI_OUTPUT);

    //how many detail levels (1 = just the capture res, > 1 goes down by half each level, 4 max)
	//int num_levels = 1;
    cam = StartCamera(CAMERA_WIDTH, CAMERA_HEIGHT,30,1,true);
    if (cam == NULL)
    {
        printf(" Camera initialization failure\n");
        return -2;
    }
    // screen parameters


    spi_h = spiOpen(0,5000,0);
    if (spi_h<0)
    {
        printf("SPI failure\n");
        return -3;
    }
    // success
    // give camera time to settle
    sleep(1);
    return 0;

}

int init(int d_lev)
{
    disp_level = d_lev;
    int res=init_hardware();
    return res;
}

/*********************MOTOR*************************/
// sets motor speed and direction
int set_motor(int motor,int speed)
{
    if ((motor>2)||(motor<0))
    {
        printf("Wrong motor number\n");
        return -1;
    }

    if ((speed>255)||(speed<-255))
    {
        printf("Speed should be in range -255..255\n");
        return -3;
    }

    // set PWM for motor1
    if (motor == 1)
    {
        if (speed >= 0)
        {
           gpioPWM(12,speed);
           gpioPWM(16,0);
        }
        if ( speed <0 )
        {
           gpioPWM(16,0-speed);
           gpioPWM(12,0);
        }
    }
    // set PWM for motor 2
    if (motor == 2)
    {
        if (speed>=0)
        {
           gpioPWM(20,speed);
           gpioPWM(21,0);
        }
        if ( speed < 0)
        {
           gpioPWM(21,0-speed);
           gpioPWM(20,0);
        }
    }
    return 0;
}

/*******CAMERA FUNCTIONS****************/

// takes camera picture and stores it into mybuff
int take_picture()
{
   if (disp_level>0)
   {
      printf("Taking camera picture\n");
   }
   cam->ReadFrame(0,&(pixels_buf[0]),sizeof(pixels_buf));
   usleep(30000);  //just in case
   return 0;
}

int save_picture(char fn[5])
{
          //save image into ppm file
        FILE *fp;
        char fname[9];
        sprintf(fname,"%s.ppm",fn);
        if (disp_level>0)
        {
           printf("Saving picture. %s\n",fname);
        }
        fp = fopen(fname,"wb");
        if ( !fp)
        {
           printf("Unable to open the file\n");
           return -1;
        }
        // write file header
        fprintf(fp,"P6\n %d %d %d\n",CAMERA_WIDTH , CAMERA_HEIGHT,255);
        int ind = 0;
        int row = 0;
        int col = 0;
        char red;
        char green;
        char blue;
        for ( row = 0 ; row < CAMERA_HEIGHT; row++)
        {
           for ( col = 0 ; col < CAMERA_WIDTH; col++)
           {
		     red =  pixels_buf[ind];
		     green =  pixels_buf[ind+1];
		     blue =  pixels_buf[ind+2];
		     fprintf(fp,"%c%c%c",red,green,blue);
		     ind = ind + 4;
           }
        }
        fflush(fp);
        fclose(fp);
        //system("timeout 1s gpicview im1.ppm");
        return 0;

}


// returns color component (color==0 -red,color==1-green,color==2-blue
// color == 3 - luminocity
// for pixel located at
char get_pixel(int col, int row, int color)
{
    // calculate address in 1D array of pixels
    int address = CAMERA_WIDTH*row*4 + col*4;
    if ((row < 0 ) || (row > CAMERA_HEIGHT) )
    {
        printf("row is out of range\n");
        return -1;
    }
    if ( (col< 0) || (col > CAMERA_WIDTH))
    {
        printf("column is out of range\n");
        return -1;
    }


    if (color==0)
    {
        return (pixels_buf[address]);
    }
    if (color==1)
    {
        return (pixels_buf[address + 1]);
    }
    if (color==2)
    {
        return (pixels_buf[address + 2]);
    }
    if (color==3)
    {
        char y = (pixels_buf[address] + pixels_buf[address+1] +pixels_buf[address+2])/3;
        return y;
    }
    printf("Color encoding wrong: 0-red, 1-green,2-blue,3 - luminosity\n");
    return -2; //error
}

int set_pixel(int col, int row, char red, char green,char blue)
{
    int address = CAMERA_WIDTH*row*4 + col*4;
    if ((address < 0) || (address>CAMERA_WIDTH*CAMERA_HEIGHT*4))
    {
        printf("SetPixel(): wrong x,y coordinates\n");
        return -1;
    }
    pixels_buf[address] = red;
    pixels_buf[address+1] = green;
    pixels_buf[address+2] = blue;
    return 0;
}

/*
void GetLine(int row,int threshold)
{

	printf("Running frame loop\n");

		int i = 0;
		int num_levels = 1;
        int texidx = (i / 30)%num_levels;

		//lock the chosen frame buffer, and copy it directly into the corresponding open gl texture
		//const void* frame_data;
		//int frame_sz;
		printf("i = %d texidx=%d\n",i,texidx);

        cam->ReadFrame(texidx,&(pixels_buf[0]),sizeof(pixels_buf));


        int ind = 0;
		//int row = 25;
		int ini_row = CAMERA_WIDTH*row*4;
		char red,green,blue; //,a;

        printf("\n");
        int col = 0;
		for (ind = ini_row ; ind < ini_row + 4*CAMERA_WIDTH; ind = ind + 4)
		{
		   red =  pixels_buf[ind];
		   green =  pixels_buf[ind+1];
		   blue =  pixels_buf[ind+2];
		   //a = mybuff[ind+3];
           Y_row[col] = ((red+green+blue)/3) >threshold;
           col = col +1;
		  // printf("ind=%d red=%d green=%d blue=%d\n",ind,red,green,blue);
		}
		int j;
		float line_error = 0.0;
        for (j=0; j < CAMERA_WIDTH;j++)
        {
            printf(" %d",Y_row[j]);
            line_error = line_error + ( j - CAMERA_WIDTH/2)*Y_row[j];
        }
        printf("\n");
        printf("line_error=%f\n",line_error);

        char v_cruise = 0;
        char v_left =  v_cruise + line_error/100.0;
        char v_right = v_cruise - line_error/100.0;

        printf(" v_left=%d v_right=%d\n",v_left,v_right);

        SetMotor(1,1,v_left);
        SetMotor(2,1,v_right);

		sleep(0.02);
		SetMotor(1,1,0);
		SetMotor(2,1,0);
        printf("\n");

}
*/

// takes camera picture and converts it
// into format for frame buffer (2 Bytes per pixel)
// fill
void convert_camera_to_screen()
{
  int x;
  int y;
  int x_offset =10;
  int y_offset =10;
  // take snapshot of original screen
  memcpy(&(cam_disp[0]),fbp,screensize);
  for ( x = 0 ; x < CAMERA_WIDTH ; x++)
   {
      for ( y = 0 ; y < CAMERA_HEIGHT; y++)
       {
		  int r = get_pixel(x,y,0);
		  int g = get_pixel(x,y,1);
		  int b = get_pixel(x,y,2);
		  if (vinfo.bits_per_pixel == 16) {
                //put_pixel_RGB565(x+x_offset, y+y_offset, r, g, b);
                 // calculate the pixel's byte offset inside the buffer
                 // note: x * 2 as every pixel is 2 consecutive bytes
                 unsigned int pix_offset = (x+x_offset) * 2 +( y+y_offset) * finfo.line_length;
                 // now this is about the same as 'fbp[pix_offset] = value'
                 // but a bit more complicated for RGB565
                 //unsigned short c = ((r / 8) << 11) + ((g / 4) << 5) + (b / 8);
                 unsigned short c = ((r / 8) * 2048) + ((g / 4) * 32) + (b / 8);
                 // write 'two bytes at once'
                 *((unsigned short*)(cam_disp + pix_offset)) = c;
            }
            else {
                // calculate the pixel's byte offset inside the buffer
                // note: x * 3 as every pixel is 3 consecutive bytes
                unsigned int pix_offset = (x+x_offset) * 3 + (y+y_offset) * finfo.line_length;
                // now this is about the same as 'fbp[pix_offset] = value'
                 *((char*)(cam_disp + pix_offset)) = b;
                 *((char*)(cam_disp + pix_offset + 1)) = g;
                 *((char*)(cam_disp + pix_offset + 2)) = r;
                //put_pixel_RGB24(x+x_offset, y+y_offset, r, g, b);
            }
       }
    }

}


int open_screen_stream()
{
    //char *fbp = 0;
   //struct fb_var_screeninfo vinfo;
   //struct fb_fix_screeninfo finfo;

    fbfd = 0;
    //struct fb_var_screeninfo orig_vinfo;
    screensize = 0;
    res=-1;
    // camera image converted to fit display depth - somewhat big for 1960x1050 screen
    //char cam_disp[3528000];
    // original image on the screen
    //char original[3528000];

    // Open the file for reading and writing
    fbfd = open("/dev/fb0", O_RDWR);
    if (fbfd == -1) {
      printf("Error: cannot open framebuffer device: %s\n",strerror(errno));
      return(1);
    }
    if (disp_level>0)
    {
      printf("The framebuffer device was opened successfully.fbfd=%d\n",fbfd);
    }

    // Get variable screen information
    res = ioctl(fbfd, FBIOGET_VSCREENINFO, &vinfo);
    if (res == -1) {
      printf("Error reading variable information: %s\n",strerror(errno));
    }
    if (disp_level>0)
    {
      printf("Original %dx%d, %dbpp\n", vinfo.xres, vinfo.yres,
                                      vinfo.bits_per_pixel );
    }
    // Store for reset (copy vinfo to vinfo_orig)
    memcpy(&orig_vinfo, &vinfo, sizeof(struct fb_var_screeninfo));

    // Get fixed screen information
    if (ioctl(fbfd, FBIOGET_FSCREENINFO, &finfo)) {
      printf("Error reading fixed information.\n");
    }

    // map fb to user mem
    screensize = vinfo.xres * vinfo.yres * vinfo.bits_per_pixel / 8;
    if (disp_level>0)
    {
       printf("screensize=%ld\n",screensize);
    }
    fbp = (char*)mmap(0,
              screensize,
              PROT_READ | PROT_WRITE,
              MAP_SHARED,
              fbfd,
              0);

    if ((int)fbp == -1) {
        printf("Failed to mmap display.\n");
        return -1;
    }

    return 0;
}

int close_screen_stream()
{
   munmap(fbp, screensize);
   if (ioctl(fbfd, FBIOPUT_VSCREENINFO, &orig_vinfo)) {
        printf("Error re-setting variable information.\n");
        return -1;
   }
   close(fbfd);
   return 0;
}

int update_screen()
{
   if ((int)fbp == -1) {
        printf("UpdateScreen() - no screen buffer handle\n");
        return -1;
   }
   //  memcpy(&(cam_disp[0]),fbp,screensize);
   // modify cam_disp with camera image
   convert_camera_to_screen(); //
    // copy original sceen fb to "original" buffer
   //memcpy(&(original[0]),fbp,screensize);
   // original screen -> cam_disp
   //memcpy(&(cam_disp[0]),fbp,screensize);
   // put cam_disp to screen
   memcpy(fbp,&(cam_disp[0]),screensize);
   usleep(3000);
   return 0;
}



int display_picture(int delay_sec,int delay_usec)
{
   open_screen_stream();
   // copy original sceen fb to "original" buffer
   memcpy(&(original[0]),fbp,screensize);
   // original screen -> cam_disp
  // memcpy(&(cam_disp[0]),fbp,screensize);
   // update camera portion of the screen
   update_screen();
   sleep(delay_sec);
   usleep(delay_usec);
   // put original image back
   memcpy(fbp,&(original[0]),screensize);
   close_screen_stream();
   // cleanup

   return 0;

}

/*******************/
/*******************INPUT/output*********************/
/************/
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

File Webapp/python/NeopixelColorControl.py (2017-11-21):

"""
NeoPixel library strandtest example
Author: Elf Eldridge
Direct port of the Arduino NeoPixel library strandtest example. 
Flashes 2 neopixels specific colours for a set length of time
"""
import time
from neopixel import *

# LED strip configuration:
LED_COUNT = 18 # Number of LED pixels.
LED_PIN = 18 # GPIO pin connected to the pixels (must support PWM!).
LED_FREQ_HZ = 800000# LED signal frequency in hertz (usually 800khz)
LED_DMA = 5 # DMA channel to use for generating signal (try 5)
LED_BRIGHTNESS = 125 # Set to 0 for darkest and 255 for brightest
LED_INVERT = False # True to invert the signal (when using NPN transistor level shift)


# Define functions which animate LEDs in various ways.
def colorwipe(strip, color, wait_ms=1):
    """Wipe color across display a pixel at a time."""
    for k in range(strip.numPixels()):
        strip.setPixelColor(k, color)
        strip.show()
        time.sleep(wait_ms/1000.0)
        strip.setPixelColor(k, color)
        strip.show()
        time.sleep(wait_ms/1000.0)

# Main program logic follows:
if __name__ == '__main__':
	# Create NeoPixel object with appropriate configuration.
    STRIP = Adafruit_NeoPixel(LED_COUNT, LED_PIN, LED_FREQ_HZ, LED_DMA, LED_INVERT, LED_BRIGHTNESS)
	# Intialize the library (must be called once before other functions).
    STRIP.begin()
    
    #wait for use to place eye on device
    time.sleep(2.5)
    
    #time to between cycles at end
    NADAWAIT = 5 #Seconds
    
    REDON = 2#0.5
    BLUEON = 0.5#0.5
    NUMBEROFCYCLES = 1

	#setup number of cycles
    for i in range(0, NUMBEROFCYCLES, 1):
        print "Off for "+str(NADAWAIT)+" seconds" 
        #for i in range(10):
        colorwipe(STRIP, Color(0, 0, 0))
        time.sleep(NADAWAIT)
        #print("Red on for "+str(REDON)+" seconds")
        #colorwipe(STRIP, Color(0, 0, 255))
        #time.sleep(REDONon)
        print "Blue on for "+str(BLUEON)+" seconds" 
        colorwipe(STRIP, Color(0, 255, 0))
        time.sleep(BLUEON)
        print "Off for "+str(NADAWAIT)+" seconds" 
        #for i in range(10):
        colorwipe(STRIP, Color(0, 0, 0))
        time.sleep(NADAWAIT)

    print "All Neos off"
    #wait for 5 seconds
    colorwipe(STRIP, Color(0, 0, 0))
    time.sleep(NADAWAIT)

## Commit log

2016-07-17 Goggles, IR processing code (complete with normalisation bug)
    [goggle.scad, goggle.stl, gogglev2.scad]
2016-07-18 Improved scaling
    [gogglev3.scad]
2016-07-19 INset for LEDs
    [goggle.stl, gogglev4.scad, gogglev5.scad]
2016-07-20 upgraded goggle
    [goggle.stl, gogglev5.scad]
2016-07-28 new goggles including diffuser and corrected LED placement
    [goggle2.stl, gogglev5.scad, gogglev6.scad]
2016-07-28 Add files via upload
    Example images obtained from camera
2016-08-02 Did stuff!
    [goggle2.stl, gogglev6.scad]
2016-08-03 added image grabber to improve framerates
2016-11-21 Added missing iPhone dev files
    [goggle_phone_v1.scad, goggle_phone_v1.stl]
2016-11-28 Converted existing scad file to sketchup format
    [Converted Sketchup file in development.skp]
2016-11-28 Converted SCAD file to sketchup format
    [Converted Sketchup file in development.skp]
2016-12-12 plotted Kaps’s data by frame and timestamp
2016-12-12 Begun Downloading a new part
    [Eyecup.stp, EyecupGrabcad V1.0.SLDPRT, goggle v2.0.SLDPRT, goggle v2.1 import to skp test - Copy.stl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]
2016-12-13 Upgraded plot with some basic filtering and stat calculations
2016-12-15 Update README.md
    UPdated readme with current progress
2016-12-15 Added Backplate to scaled Grabcad eyepiece. Project Calculations file included
    [EyecupGrabcad V1.0.SLDPRT]
2016-12-21 Holder and Eyepiece seperated and joined in Assembly
    [EyecupGrabcad V1.0.SLDPRT, Eyepiece and Neoholder v1.0 - Eyepiece-1.STL, Eyepiece and Neoholder v1.0 - LED-Neo-Cam Holder V1.0-1.STL, Eyepiece and Neoholder.SL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]
2016-12-21 Cleanup early goggles
    [goggle.scad, goggle.stl, goggle2.stl, goggle_phone_v1.stl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]
2017-01-10 Lots of models!!!!!!
    [Adafruit NeoPixel Ring 16.brd, Adafruit NeoPixel Ring 16.sch, EyecupGrabcad V1.0.SLDPRT, Eyepiece and Neoholder.SLDASM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]
2017-02-02 Image and Eye Modelling Dump
    [Eyepiece V1.1.SLDPRT, Eyepiece V1.1.STL, Eyepiece V1.2.SLDPRT, Eyepiece V1.2.STL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]
2017-02-09 Downloaded 3D neopixel model
    [Altium footprints, SMD Ceramic Capacitors, 2013-06-08-1.PcbLib, Altium footprints, SMD Resistors, 2013-06-08-1.PcbLib, Baugruppe1.0002.iam, Baugruppe1.iam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]
2017-02-10 Started Enclosure design
    [Adafruit NeoPixel Ring 16.brd, Adafruit NeoPixel Ring 16.sch, Altium footprints, SMD Ceramic Capacitors, 2013-06-08-1.PcbLib, Altium footprints, SMD Resistors,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]
2017-02-13 Established Sideways plates
    [Baseplate Frame.SLDPRT, Enclosure Eastplate.SLDPRT, Enclosure Westplate.SLDPRT, Eyepiece V1.3.SLDPRT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]
2017-11-20 Reorganised everything
    [Adafruit NeoPixel Ring 16.brd, Adafruit NeoPixel Ring 16.sch, Altium footprints, SMD Ceramic Capacitors, 2013-06-08-1.PcbLib, Altium footprints, SMD Resistors,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]
